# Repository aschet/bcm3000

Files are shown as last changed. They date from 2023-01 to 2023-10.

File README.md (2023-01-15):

# BCM-3000: Beer Color Meter (Work in Progress)

While measuring specific gravity is ubiquitous in home brewing, measuring beer color in EBC/SRM units is not. One reason for this is the cost associated with the required laboratory equipment. For this reason, this project aims to develop a low-cost LED-based specialty photometer that implements the procedures defined in the <a href="https://www.mebak.org">MEBAK</a> II 2.12 and <a href="https://www.asbcnet.org">ASBC</a> Beer-10 analytical methods. All design files for the Arduino-based BCM-3000, including the <a href="https://www.kicad.org">KiCad</a> schematic and <a href="https://www.freecadweb.org">FreeCAD</a> CAD drawings for a 3D printable cuvette holder, have been published in this repository so that you can build this instrument yourself. This project is not the first attempt to create an LED-based photometer to measure beer color. Di Caro et al. (2019) and Barth et al. (2021) have already built similar devices.

<p align="center">
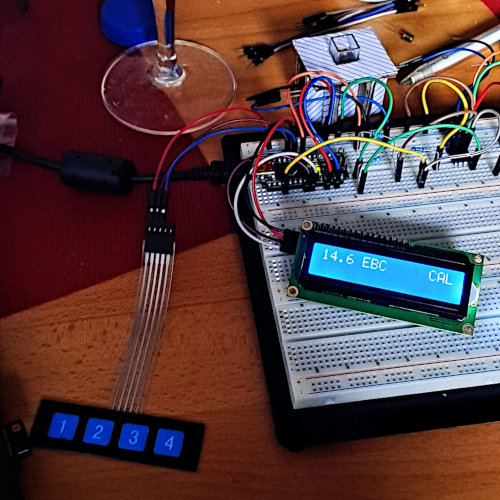
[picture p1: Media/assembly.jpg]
  
</p>

## Measurement of Beer Color

Beer color, or more precisely the intensity of beer color, is measured with a high-precision spectrophotometer (accuracy of at least +-0.5 nm) based on the Beer-Lambert law. In a measurement, the light absorption of the sample at a wavelength of 430 nm is determined against (distilled) water through a square cuvette with a path length of 10 mm. The samples must be degassed and filtered for turbidity with a membrane filter (0.45 µm) before measurement. If the filtration does not result in a clear sample, additional filtration steps must be performed, e.g. by adding 0.1 % kieselguhr to the sample and repeating the filtration. The measurement result is calculated using the following two formulas, where A is the measured absorbance at 430 nm and D is the dilution factor. Samples of dark beers may need to be diluted before measurement, otherwise they will not be measurable within the linear range of an instrument. A dilution of 1:1 corresponds to a D factor of 2. The factor 1.27 scales the absorbance from a cuvette with a path length of 10 mm to a half-inch cuvette. EBC units should be specified with two significant figures, while SRM units should be specified as degrees to one decimal place.

$$\textrm{EBC} = 25 \cdot A_{430} \cdot D$$ 

$$\textrm{SRM} = 10 \cdot 1.27 \cdot A_{430} \cdot D$$ 

The absorbance can be calculated from the measured light transmission. To determine the transmittance value, you need to measure the intensity when no light hits the detector (noise) and then when light shines through water and the sample to be measured.

$$\textrm{A} =  -\log(T)$$ 

$$\textrm{T} =  \frac{I_{\textrm{Beer}} - I_{\textrm{Noise}}}{I_{\textrm{Water}} - I_{\textrm{Noise}}}$$ 

In addition to the described analysis method, the ASBC Beer-10 also defines the tristimulus method, which requires the measurement of the entire visible light spectrum from which a unambiguous CIELAB color can be calculated. This method is not supported by the BCM-3000.

### LEDs and Calibration of Photometers

The monochromator in a spectrophotometer, e.g. an optical grating, splits the light into its components. With additional optical components, the operator can then select a specific wavelength for measurement. Similarly, LEDs can be manufactured to emit a specific peak wavelength. It should be noted that LEDs do not emit monochromatic light and may also vary within the allowable product tolerance due to the manufacturing process. Calibration and adjustment is required to compensate for these differences. Beer-10 provides a calibration procedure for photometers with a moderately wide spectral bandpass filter.

For calibration, use a filter that is transmissive in the range of 420-450 nm. Select cuvettes with a specific path length that give absorbance values between 0.187 and 0.699 (20-65% transmission) for better accuracy. Measure beers with multiple color levels using a high-precision spectrophotometer and also the photometer with a bandpass filter. Measure at least two samples in each color level. Then calculate the average value for both instruments in each level. A calibration curve can be derived from this data.

### Turbidity Detection (Not Implemented)

In addition to the procedure described above, the ASBC establishes a criterion based on an additional absorbance measurement at a wavelength of 700 nm to determine whether a beer sample is "free of turbidity" and thus suitable for measurement:

$$A_{700} \le 0.039 \cdot A_{430}$$

### Turbidity Compensation (Not Implemented)

Although not part of a standard, several sources suggest a method to compensate for turbidity based on an absorbance measurement at a wavelength of 700 nm, since sample preparation is not always possible, e.g. for inline measurements. Please note that these are quite large corrections. "Color of Wort" (1954) suggests the following formula where optical density has been replaced by absorbance:

$$A_{430}' = A_{430} - (A_{700} - 0.039 \cdot A_{430})$$

The Chemtronic Waltemode GmbH (2012) describes a similar approach:

$$A_{430}' = A_{430} - A_{700}$$

### Carbon Dioxide Detection (Not Implemented)

To determine whether carbonization has actually been removed from a sample, Di Caro et al. (2019) measure the change in radiation on the detector side. The presence of residual carbon dioxide results in a change in the absorbed radiation. Unfortunately, they do not give a threshold for detection.

### Extended Measurement Range (Not Implemented)

At about 30 SRM or about 60 EBC, most of the light transmitted through a sample in a cuvette with 10 mm path length is absorbed at a wavelength of 430 nm. The sample must then be diluted to obtain a meaningful measurement result. There are several measures that can be taken to measure darker beers without dilution, although these are not standard procedures. A cuvette with a shorter path length, such as 5 mm, will result in lower absorbance (measurement results must be scaled to 10 mm), but cuvettes with a path length of less than 10 mm are typically much more expensive. To obtain more accurate inline measurement results for very dark beers (up to 35 EBC), Chemtronic Waltemode GmbH (2012) suggests taking measurements at a wavelength of 550 nm instead of 430 nm because the light absorption is lower. However, a model to correlate with the absorbance at 430 nm is required. The British I.O.B. initially performed measurements at a wavelength of 530 nm before 430 nm was introduced (Seaton et al., 1993).

<p align="center">
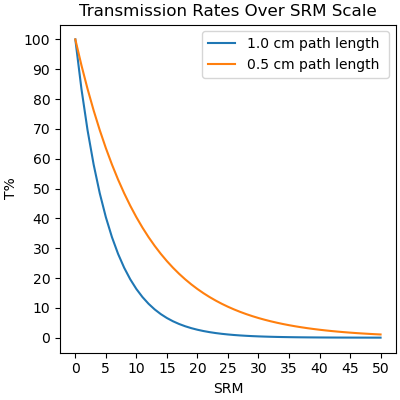
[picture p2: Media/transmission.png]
  
</p>

## Usage of the BCM-3000

* For adjustment, place a cuvette filled with (distilled) water in the cuvette holder. The transparent cuvette window should point in the direction of the triangular mark on the cuvette holder. Place the cuvette holder cap on the cuvette holder and press button 2 to start the adjustment. When adjustment is complete, the ADJ status is activated on the instrument LCD. If you press and hold the button 2 for one second, the adjustment is reset.
* For measurement, place a cuvette filled with decarbonated and non turbid beer in the cuvette holder. Place the cuvette holder cap on the cuvette holder and press button 1 to start the measurement. When the measurement is complete, the result value is displayed on the LCD of the instrument. Pressing and holding the button 1 for one second switches between EBC and SRM units.
* The holder of the BCM-3000 accepts square cuvettes with a path length of 10 mm and a height of 45 mm. The cuvettes should be suitable for visible light spectroscopy and therefore made of glass, polystyrene (PS) or polymethyl methacrylate (PMMA).

<p align="center">
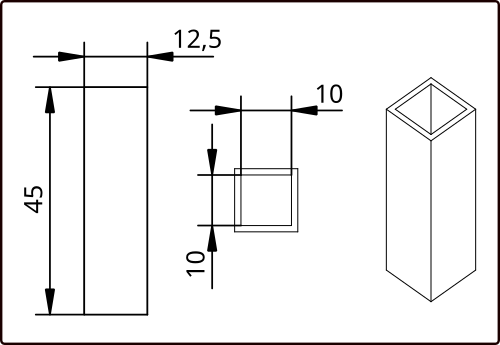
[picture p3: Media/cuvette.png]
  
</p>

## Schematic

A transimpedance amplifier (TIA) was integrated into the circuit for signal processing. The design and calculations for the TIA were derived from a reference design by Caldwell, J. (2014).

## Bill of Materials

| Description                                     | Qty |
| ---                                             | --- |
| Arduino Nano                                    | 1   |
| Mini USB cable                                  | 1   |
| USB power adapter                               | 1   |
| Everlight 333-2UBC/C430 LED                     | 1   |
| Osram SFH 203 photodiode                        | 1   |
| Microchip MCP6002-I/P op amp                    | 1   |
| Joy-IT 16x2 LCD module                          | 1   |
| Push button                                     | 2   |
| Board                                           | 1   |
| Soldering and wiring material                   | 1   |
| 22 pF capacitor                                 | 1   |
| 60 Ω resistor                                   | 1   |
| 270 Ω resistor                                  | 1   |
| 14 kΩ resistor                                  | 1   |
| 560 kΩ resistor                                 | 2   |
| Custom cuvette holder                           | 1   |
| Custom cuvette holder cap                       | 1   |
| Housing                                         | 1   |
| Square cuvette, 10 mm path length, 45 mm height | 1   |

## Open Issues and Limitations

* Currently, the instrument does not provide satisfactory measurement results. The darker a beer is, the higher the deviation from the expected measured value.
* Integration of optical components with a narrower spectral bandwidth.
* Calibration procedure to compensate for the spectral characteristics of the LED used.
* Evaluation of the accurracy and repeatabillity as well as the suitable measurement range.
* For diluted samples, the dilution factor itself must be included in the measurement result.
* The instrument does not have a temperature compensation.

## References

* <a href="https://doi.org/10.1080/03610470.2020.1807888">Barth, R., Rieger, R. H., & Kim, Y. (2021). Ruggedized color measurement for beer, wort, and malt. Journal of the American Society of Brewing Chemists. American Society of Brewing Chemists, 79(1), 41-45.</a>
* <a href="https://www.ti.com/lit/pdf/tidu535">Caldwell, J. (2014). 1 MHz, Single-Supply, Photodiode Amplifier Reference Design.</a>
* <a href="https://www.chemtronic-gmbh.de/images/chemtronic/Apps_e_pdf/EBC%20Colour%20I.pdf">Chemtronic Waltemode GmbH. (2012). EBC-Colour Measurement.</a>
* <a href="https://doi.org/10.1080/00960845.1954.12006433">Color of Wort. (1954). Proceedings Annual Meeting - American Society of Brewing Chemists, 12(1), 168–170.</a>
* <a href="https://doi.org/10.1109/MetroAgriFor.2019.8909213">Di Caro, D., Liguori, C., Pietrosanto, A., & Sommella, P. (2019). A low-cost device for beer color measurement. 2019 IEEE International Workshop on Metrology for Agriculture and Forestry (MetroAgriFor).</a>
* <a href="https://doi.org/10.1002/j.2050-0416.1993.tb01140.x">Seaton, J. C., Cantrell, I. C., & Submitted on Behalf of the institute of Brewing Analysis Committee. (1993). The determination of beer colour-collaborative trial. Journal of the Institute of Brewing. Institute of Brewing (Great Britain), 99(1), 21–23.</a>
* <a href="https://www.asbcnet.org/Methods/Pages/default.aspx">Technical Committe, A. (2011). Color. In ASBC Methods of Analysis. American Society of Brewing Chemists.</a>

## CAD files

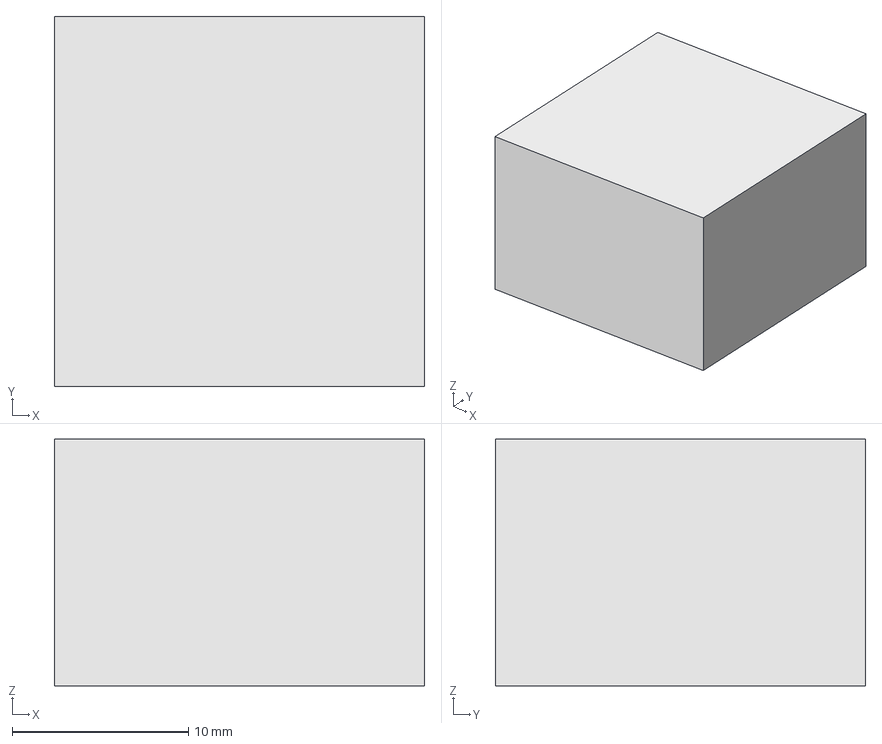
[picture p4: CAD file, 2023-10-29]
Drawings/cuvette_holder_cap.FCStd
21.0 x 21.0 x 14.0 mm

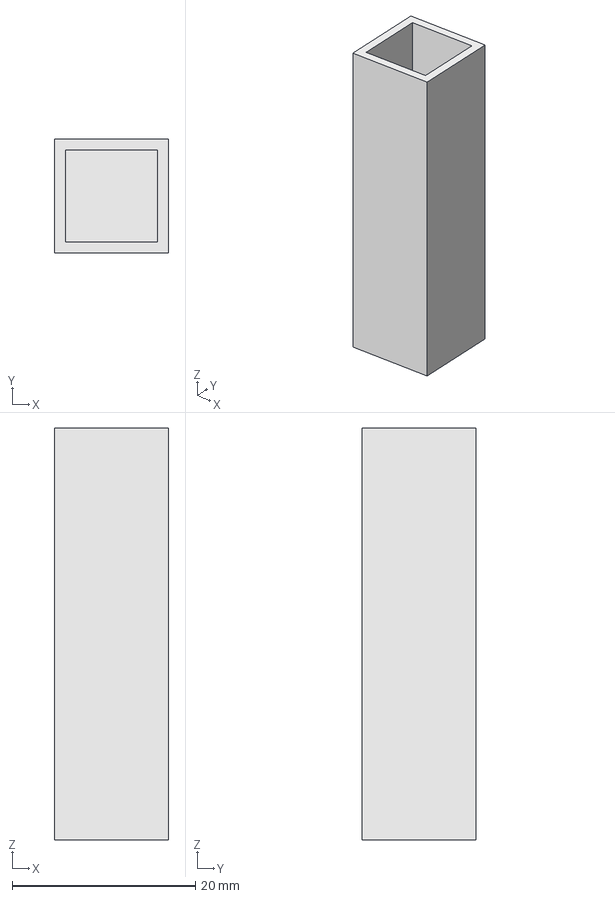
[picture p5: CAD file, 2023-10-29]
Drawings/cuvette.FCStd
12.5 x 12.5 x 45.0 mm

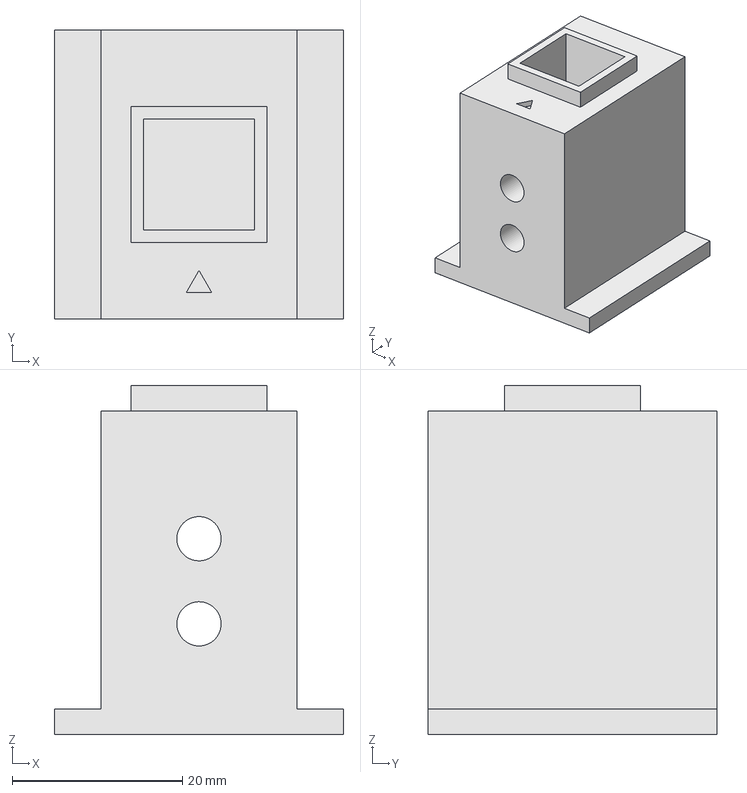
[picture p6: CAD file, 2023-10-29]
Drawings/cuvette_holder.FCStd
34.0 x 34.0 x 41.0 mm

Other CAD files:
Drawings/cuvette_holder.stl
Drawings/cuvette_holder_cap.stl

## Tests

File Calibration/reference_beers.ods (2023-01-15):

Name | EBC | A430 | T430
Blanche de Namur | 6 | 0,24 | 0,57544
Duvel | 6 | 0,24 | 0,57544
Hoegaarden | 6 | 0,24 | 0,57544
Mongozo Premium Pilsener | 6 | 0,24 | 0,57544
Stella Artois | 6 | 0,24 | 0,57544
Averbode | 8 | 0,32 | 0,47863
Delirium Tremens | 9 | 0,36 | 0,43652
Saison Dupont | 9 | 0,36 | 0,43652
Budweiser Budvar Original | 10 | 0,40 | 0,39811
Judas | 10 | 0,40 | 0,39811
Satan Gold | 10 | 0,40 | 0,39811
Westmalle Tripel | 10 | 0,40 | 0,39811
Affligem Blond | 11 | 0,44 | 0,36308
Houblon Choffe dobbelen IPA Tripel | 11 | 0,44 | 0,36308
La Trappe Blond | 11 | 0,44 | 0,36308
Brigand | 12 | 0,48 | 0,33113
Grimbergen Blond | 12 | 0,48 | 0,33113
Leffe Triple | 12 | 0,48 | 0,33113
Achel 8 Blond | 13 | 0,52 | 0,30200
La Chouffe | 13 | 0,52 | 0,30200
Leffe Blonde | 14 | 0,56 | 0,27542
Chimay Triple | 16 | 0,64 | 0,22909
Piraat | 22 | 0,88 | 0,13183
Orval | 23 | 0,92 | 0,12023
La Trappe Quadrupel | 28 | 1,12 | 0,07586
Rochefort 6 | 31 | 1,24 | 0,05754
Chimay Rouge | 32 | 1,28 | 0,05248
Kasteel Rouge | 43 | 1,72 | 0,01905
Rochefort 8 | 45 | 1,80 | 0,01585
St. Bernardus Pater 6 | 45 | 1,80 | 0,01585
Achel 8 Bruin | 52 | 2,08 | 0,00832
St. Bernardus Prior 8 | 52 | 2,08 | 0,00832
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

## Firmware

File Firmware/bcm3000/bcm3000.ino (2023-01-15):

// Arduino Firmware for BCM-3000 Beer Color Meter
// Copyright 2023 Thomas Ascher <thomas.ascher@gmx.at>
// SPDX-License-Identifier: MIT
//
// Install the following libraries via the library manager:
// EasyButton 2.0.1, LiquidCrystal I2C 1.1.2, fp64lib 1.1.20

#define DEBUG_SERIAL
#define HIGH_PRECISION

#ifdef HIGH_PRECISION
  #include "double.h"
  typedef Double t_double;
  float64_t& valueRef(Double& f) {
    return f.value;
  }
  const float64_t& valueRef(const Double& f) {
    return f.value;
  }
#else
  typedef double t_double;
  double& valueRef(double& f) {
    return f;
  }
  const double& valueRef(const double& f) {
    return f;
  }
#endif

#include <EEPROM.h>
#include <Wire.h>
#include <LiquidCrystal_I2C.h>
#include <EasyButton.h>

constexpr char* VERSION_DEV = "BCM-3000 MK I";
constexpr char* VERSION_SW = "1.0";
// Set the following value according to your instrument specific water intensity.
static const t_double DEFAULT_WATER_INTENSITY = 0.997;
static const t_double NAN_VALUE = NAN;
constexpr uint8_t LED_430NM_PIN = 4;
constexpr uint8_t PHD_430NM_PIN = A0;
constexpr uint8_t BTN_MEASURE_BEER_PIN = 6;
constexpr uint8_t BTN_MEASURE_WATER_PIN = 7;
constexpr uint32_t BTN_2ND_OP_DELAY = 1000;
constexpr int EEPROM_ADDR_UNIT = 0;
constexpr int EEPROM_ADDR_WATER_INTENSITY = 1;

#ifdef DEBUG_SERIAL

inline void debugPrint(const char* caption, const t_double& value) {
  Serial.print(caption);
  Serial.print(": ");
  Serial.println(value, 4);
}

#endif

class LED {
public:
  LED(uint8_t pin)
    :m_pin(pin) {
  }

  void init() {
    pinMode(m_pin, OUTPUT);
  }

  void setOn(bool on) {
    if (on) {
      digitalWrite(m_pin, HIGH);
    }
    else {
      digitalWrite(m_pin, LOW);
    }
  }

private:
  uint8_t m_pin;
};

class PhotoDiode {
public:
  PhotoDiode(uint8_t pin)
    :m_pin(pin) {
  }

  t_double read() const {
    static t_double VOLTAGE_DIVISOR = 1024;
    t_double voltage = analogRead(m_pin);
    return voltage / VOLTAGE_DIVISOR;
  }

  t_double readAverage() const {
    constexpr uint8_t NUMBER_READS = 10;
    const t_double READS_DIVISOR = NUMBER_READS;
    t_double value = 0.0;
    for (uint8_t i = 0; i < NUMBER_READS; ++i) {
      value += read();
      delay(50);
    }
    value /= READS_DIVISOR;
    return value;    
  }

private:
  uint8_t m_pin;
};

bool isUnitEBC = true;
t_double waterIntensity = DEFAULT_WATER_INTENSITY;
t_double beerIntensity = NAN_VALUE;

LiquidCrystal_I2C lcd(0x27, 16, 2);
LED led430NM(LED_430NM_PIN);
PhotoDiode phd430NM(A0);
EasyButton btnMeasureWater(BTN_MEASURE_WATER_PIN);
EasyButton btnMeasureBeer(BTN_MEASURE_BEER_PIN);

void printUnit() {
  lcd.setCursor(6, 0);
  if (isUnitEBC) {
    lcd.print(" EBC");
  } else {
    lcd.print(" SRM");    
  }
}

void storeUnit() {
  EEPROM.put(EEPROM_ADDR_UNIT, isUnitEBC);
}

void restoreUnit() {
  EEPROM.get(EEPROM_ADDR_UNIT, isUnitEBC);
  printUnit();
}

void printAdjustStatus(bool on) {
  lcd.setCursor(0, 0);
  if (on) {
    lcd.print("ADJ");
  } else {
    lcd.print("   ");
  }
}

void storeWaterIntensity() {
  EEPROM.put(EEPROM_ADDR_WATER_INTENSITY, valueRef(waterIntensity));
}

void clearWaterIntensity() {
  EEPROM.put(EEPROM_ADDR_WATER_INTENSITY, valueRef(NAN_VALUE));  
}

void restoreWaterIntensity() {
  EEPROM.get(EEPROM_ADDR_WATER_INTENSITY, valueRef(waterIntensity));
  if (isnan(waterIntensity)) {
    waterIntensity = DEFAULT_WATER_INTENSITY;
  } else {
    printAdjustStatus(true);
  }
}

t_double correlaeToA430(const t_double& abs) {
  // Generate this calibration polynomial with the calibration.py file
  return t_double(7.2563e-01)+abs*(t_double(-2.0034e+00)+abs*(t_double(2.1415e+00)));
} 

void printMeasurement() {
  if (isnan(beerIntensity))
    return;

  static const t_double NEGATIVE_SIGN = -1.0;
  t_double a430 = log10(beerIntensity / waterIntensity) * NEGATIVE_SIGN;
#ifdef DEBUG_SERIAL
  debugPrint("abs", a430);
#endif

  a430 = correlaeToA430(a430);

  static const t_double SRM_FACTOR = 12.7;
  static const t_double EBC_FACTOR = 25.0;
  t_double value = isUnitEBC ? a430 * EBC_FACTOR : a430 * SRM_FACTOR;
  
  static const t_double RESULT_MIN = 0.0;
  static const t_double RESULT_MAX = 999.0;
  if (value < RESULT_MIN) {
    value = RESULT_MIN;
  } else if (value > RESULT_MAX) {
    value = RESULT_MAX;
  }
  
  constexpr int VALUE_BUFFER_SIZE = 6;
  static char valueBuffer[VALUE_BUFFER_SIZE];
  dtostrf(value, VALUE_BUFFER_SIZE - 1, 1, valueBuffer);
  lcd.setCursor(11, 0);
  lcd.print(valueBuffer);
}

t_double measureIntensity() { 
  t_double noise = phd430NM.readAverage();  
#ifdef DEBUG_SERIAL
  debugPrint("noise", noise);
#endif
  led430NM.setOn(true);
  delay(250);
  t_double intensity = phd430NM.readAverage() - noise;
  led430NM.setOn(false);
#ifdef DEBUG_SERIAL
  debugPrint("intensity", intensity);
#endif  
  return intensity;
}

void onMeasureWater() {
#ifdef DEBUG_SERIAL
  Serial.println("measure water");
#endif
  waterIntensity = measureIntensity();
  storeWaterIntensity();
  printAdjustStatus(true);
  printMeasurement();
}

void onResetWater() {
  waterIntensity = DEFAULT_WATER_INTENSITY;
#ifdef DEBUG_SERIAL
  Serial.println("reset water");
#endif
  clearWaterIntensity();
  printAdjustStatus(false);
  printMeasurement();
}

void onMeasureBeer() {
#ifdef DEBUG_SERIAL
  Serial.println("measure beer");
#endif  
  beerIntensity = measureIntensity();
  printMeasurement();
}

void onChangeUnit() {
  isUnitEBC = !isUnitEBC;
#ifdef DEBUG_SERIAL
  Serial.print("change unit: ");
  if (isUnitEBC) {
    Serial.println("EBC");
  } else {
    Serial.println("SRM");
  }
#endif
  storeUnit();
  printUnit();
  printMeasurement();
}

void setup() {
#ifdef DEBUG_SERIAL
  Serial.begin(9600);
#endif
  lcd.init();
  lcd.clear();
  lcd.backlight();
  lcd.setCursor(0, 0);
  lcd.print(VERSION_DEV);
  lcd.setCursor(0, 1);
  lcd.print("SW: v");
  lcd.print(VERSION_SW);
  led430NM.init();
  btnMeasureWater.begin();
  btnMeasureWater.onPressed(onMeasureWater);
  btnMeasureWater.onPressedFor(BTN_2ND_OP_DELAY, onResetWater);
  btnMeasureBeer.begin();
  btnMeasureBeer.onPressed(onMeasureBeer);
  btnMeasureBeer.onPressedFor(BTN_2ND_OP_DELAY, onChangeUnit);
  delay(3000);
  lcd.clear();
  restoreWaterIntensity();
  restoreUnit();
}

void loop() {
  btnMeasureWater.read();
  btnMeasureBeer.read();
}

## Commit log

2023-01-15 Initial import
    [bcm3000.kicad_pcb, bcm3000.kicad_sch, cuvette.FCStd, cuvette_holder.FCStd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]
2023-02-01 added capacitors, disabled 2nd op amp
    [bcm3000.kicad_sch]
2023-10-29 updated sw version
    [cuvette.FCStd, cuvette_holder.FCStd, cuvette_holder_cap.FCStd]
